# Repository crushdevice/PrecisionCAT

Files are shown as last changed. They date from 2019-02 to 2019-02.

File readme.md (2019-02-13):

PrecisionCAT Software, Hardware Blueprints and Associated Documentation Files
The MIT License (MIT) Copyright (c)

Permission is hereby granted, free of charge, to any person obtaining a copy of this software, hardware blueprints and associated documentation files (the "crush files"), to deal in the crush files without restriction, including without limitation the rights to use, copy, modify, merge, publish, distribute, sublicense, and/or sell copies of the crush files, and to permit persons to whom the crush files is furnished to do so, subject to the following conditions:

The above copyright notice and this permission notice shall be included in all copies or substantial portions of the Software.

THE CRUSH FILES IS PROVIDED "AS IS", WITHOUT WARRANTY OF ANY KIND, EXPRESS OR IMPLIED, INCLUDING BUT NOT LIMITED TO THE WARRANTIES OF MERCHANTABILITY, FITNESS FOR A PARTICULAR PURPOSE AND NONINFRINGEMENT. IN NO EVENT SHALL THE AUTHORS OR COPYRIGHT HOLDERS BE LIABLE FOR ANY CLAIM, DAMAGES OR OTHER LIABILITY, WHETHER IN AN ACTION OF CONTRACT, TORT OR OTHERWISE, ARISING FROM, OUT OF OR IN CONNECTION WITH THE CRUSH FILES OR THE USE OR OTHER DEALINGS IN THE CRUSH FILES.

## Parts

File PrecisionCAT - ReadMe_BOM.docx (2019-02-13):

# PrecisionCAT GitHub Information

Defining the Relationship Between Stress from

Graspers and Bowel Injury in Humans to Establish

Intraoperative Force Boundaries

Khan, Amanda; University of Toronto - Institute of Biomaterials and Biomedical Engineering

MacDonald, Matthew; CIGITI – Hospital for Sick Children, Toronto, ON

Doshi, Sachin; CIGITI – Hospital for Sick Children, Toronto, ON

Streutker, Catherine; University of Toronto Department of Laboratory Medicine and Pathobiology

Rowsell, Corwyn; University of Toronto Department of Laboratory Medicine and Pathobiology

Drake, James; Hospital For Sick Children, Surgery, Neurosurgery, Toronto, ON

Grantcharov, Teodor; University of Toronto Department of Surgery

* Materials and correspondence to: Amanda Farah Khan, amy.khan@mail.utoronto.ca

# Read Me

All SolidWorks and .stl CAD files necessary to manufacture and recreate the PrecisionCAT along with the full Python code necessary to interact with the controller and experimental protocol is located on GitHub and is licensed under the MIT Open Source Initiative:

https://github.com/crushdevice

Load all part files in the PrecisionCAT folder with the main SolidWorks assembly file “PrecisionCATASSEMBLY.SLDASM”.

# Build of Materials

Part | Description | Product Code
SMAC Linear Actuator | 25 mm stroke; 48 volts | https://www.smac-mca.com/lca-series-p-15.html?cPath=1_4 LCA 50-025-72-1F-3
Power Supply | 48 volt | Generic
Omega Load Cell | Miniature universal load cell with ±5 kgF range | https://www.omega.com/pptst/LCM703.html LCM703-5
LAC-1 Controller | Single axis controller; 12-48 volts | https://www.smac-mca.com/lac-single-axis-controller-p-127.html
LAC-1 Communication Kit | Used for interfacing with the controller | Bundled with LAC-1 Controller
Omega Load Cell Strain Gage Amplifier | Bridge excitation of 4 to 15 volts; adjustable gain and offset | https://www.omega.ca/en/communication-and-connectivity/signal-conditioners-and-transmitters/signal-conditioners/dmd-465-series/p/DMD-465 DMD-465
End-Feed Fastener | M6 thread for 30 mm high rail T-slotted framing | https://www.mcmaster.com/5537t527 McMaster-Carr part 5537T527
T-Slotted Framing Single Rail | 1 ft; 30 mm x 30 mm | https://www.mcmaster.com/5537t97 McMaster-Carr part 5537T97
T-Slotted Framing Corner Brackets | For 30 mm | https://www.mcmaster.com/5537t936 McMaster-Carr part 5537T936
316 Stainless Steel Threaded Rod (20 mm) | M6; 1 mm x 20 mm | https://www.mcmaster.com/98863a243 McMaster-Carr part 98863A243
316 Stainless Steel Threaded Rod (40 mm) | M6; 1 mm x 40 mm | https://www.mcmaster.com/98863a260 McMaster-Carr part 98863A260
316 Stainless Steel Thin Hex Nut (M6) | M6; 1 mm | https://www.mcmaster.com/93935a335 McMaster-Carr part 93935A335
316 Stainless Steel Thin Hex Nut (M3) | M3; 0.5 mm | https://www.mcmaster.com/93935a320 McMaster-Carr part 93935A320
Aluminum Plate | 6061 aluminum | Custom milled

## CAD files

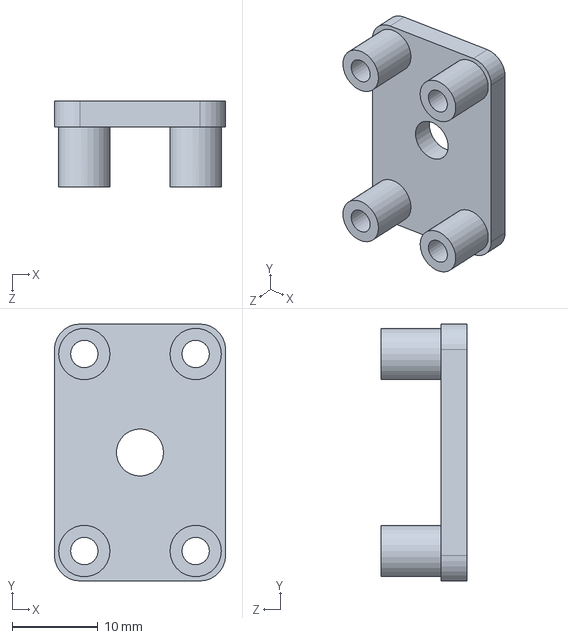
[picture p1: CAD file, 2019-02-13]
Grasper Face 1cm Holder 6mm.SLDPRT
20.0 x 30.0 x 10.0 mm

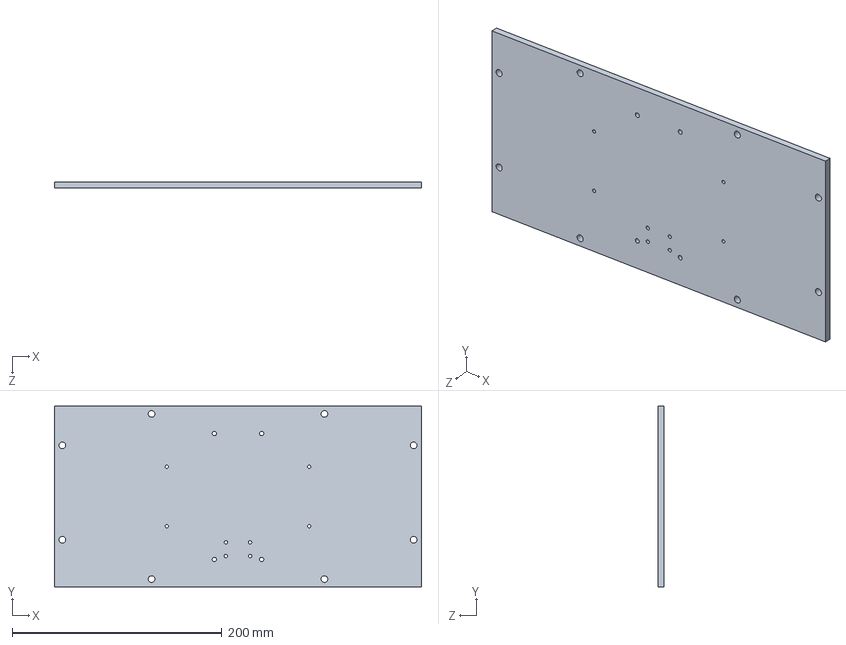
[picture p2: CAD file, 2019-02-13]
Base Plate Al 6mm.SLDPRT
349.8 x 172.5 x 6.00 mm

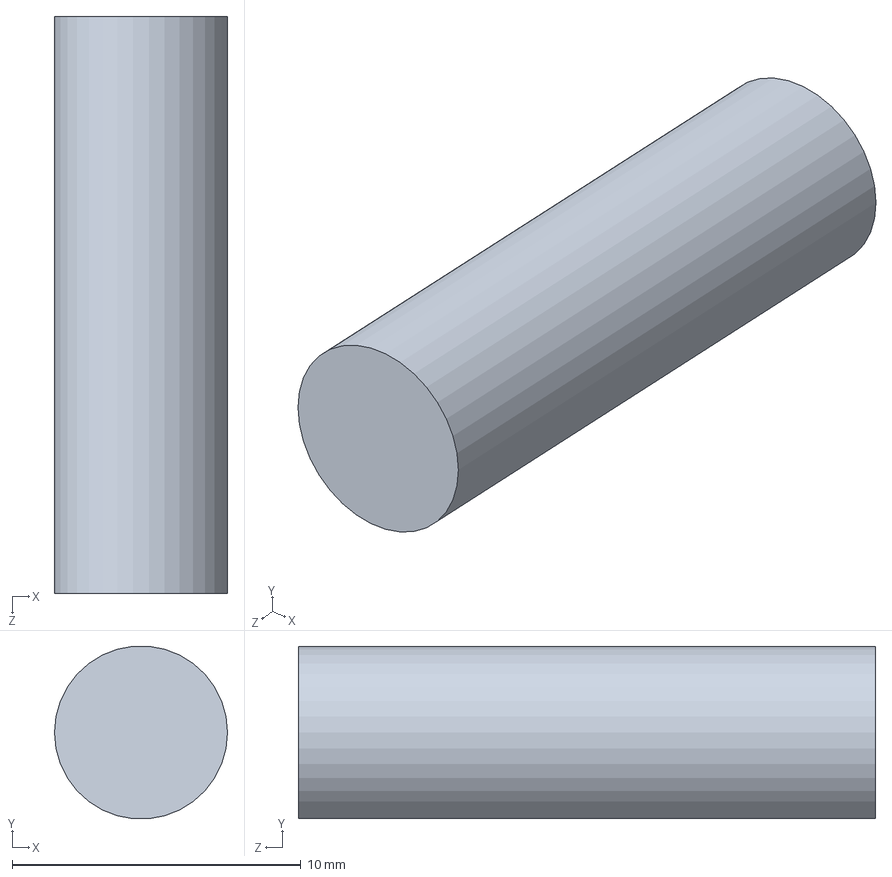
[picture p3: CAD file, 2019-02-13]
Threaded Stud M6.SLDPRT
6.00 x 5.97 x 20.0 mm

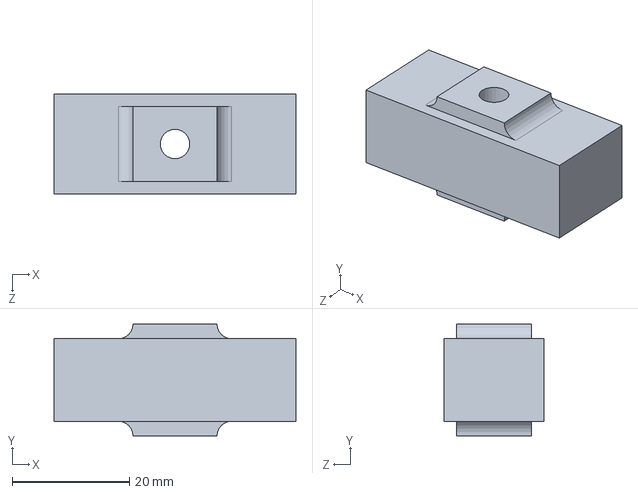
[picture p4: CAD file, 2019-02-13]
Load Cell.SLDPRT
41.2 x 19.1 x 17.1 mm

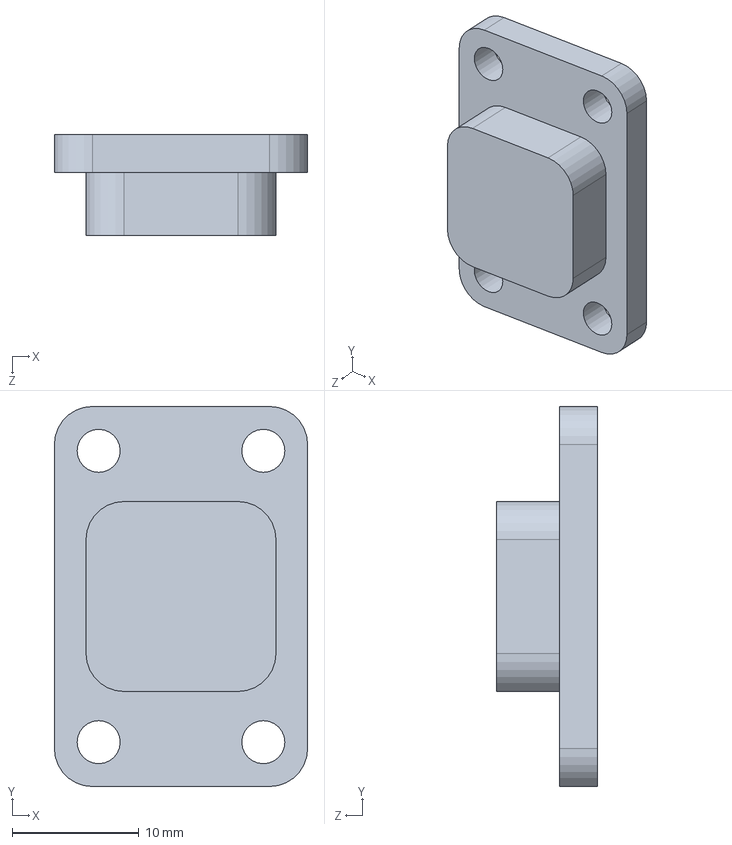
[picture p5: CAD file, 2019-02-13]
Grasper_Plate.SLDPRT
20.0 x 30.0 x 8.00 mm

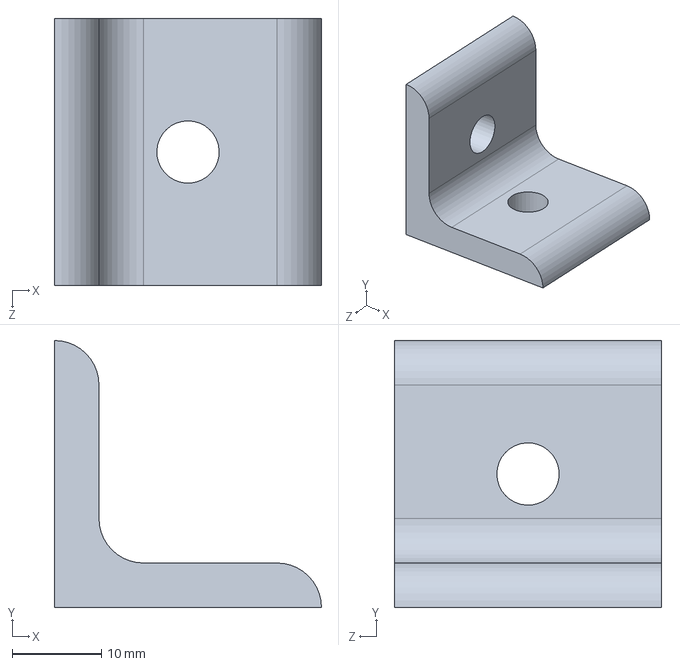
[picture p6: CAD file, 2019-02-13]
3mm_Corner_Mount.SLDPRT
30.0 x 30.0 x 30.0 mm

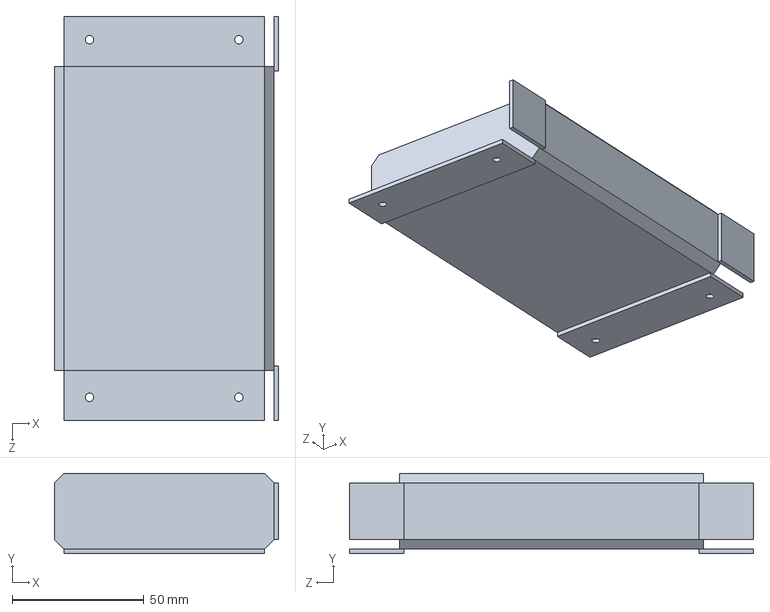
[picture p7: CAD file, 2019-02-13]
LAC-1.SLDPRT
85.2 x 30.4 x 153.2 mm

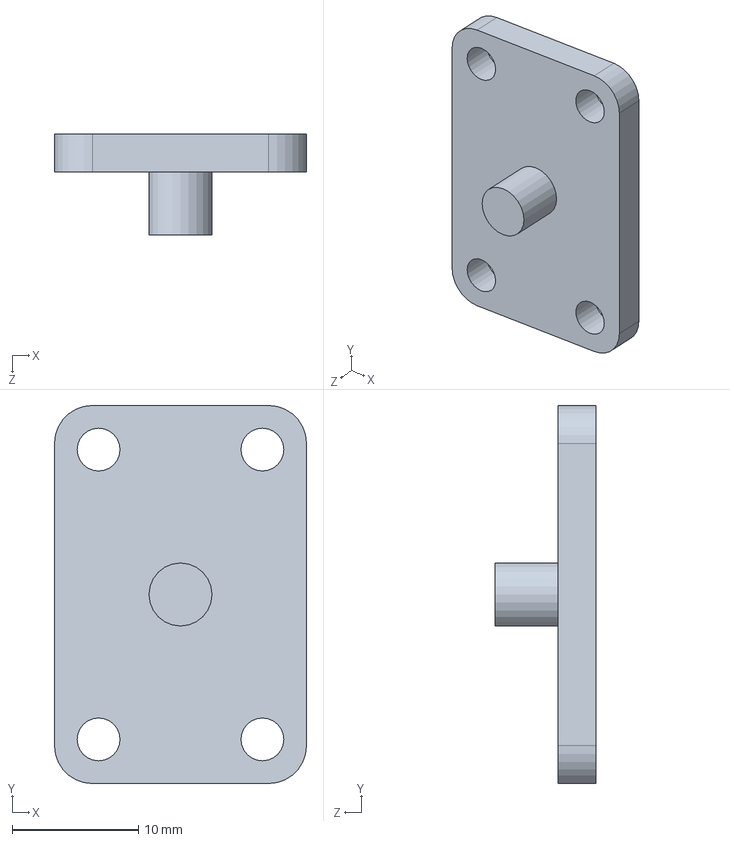
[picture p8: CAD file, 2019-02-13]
Grasper_Pin.SLDPRT
20.0 x 30.0 x 8.00 mm

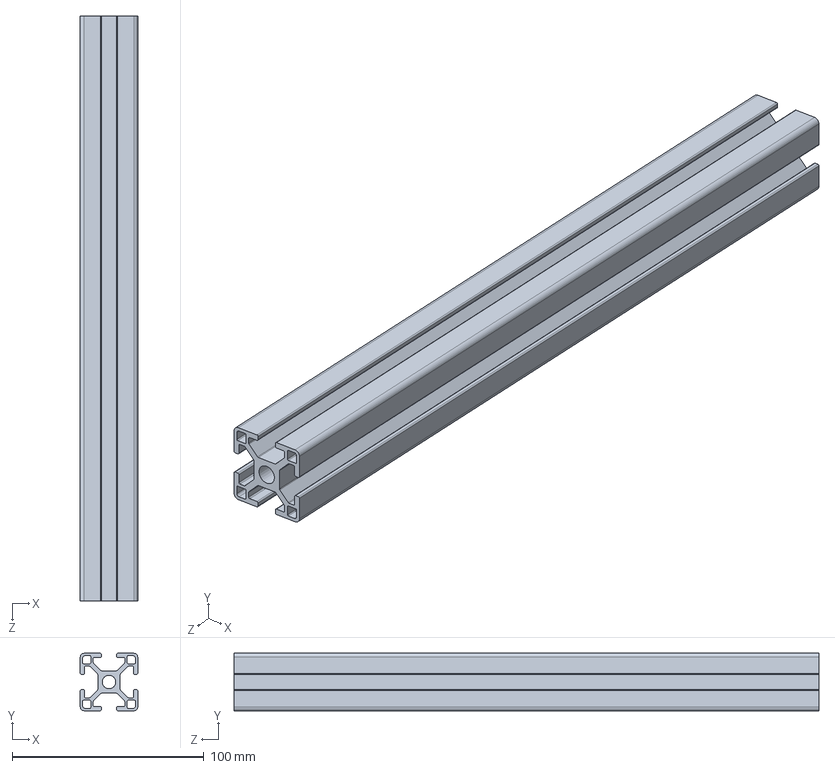
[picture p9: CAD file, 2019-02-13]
3mm_Extrusion_1ft.SLDPRT
30.0 x 30.0 x 304.8 mm

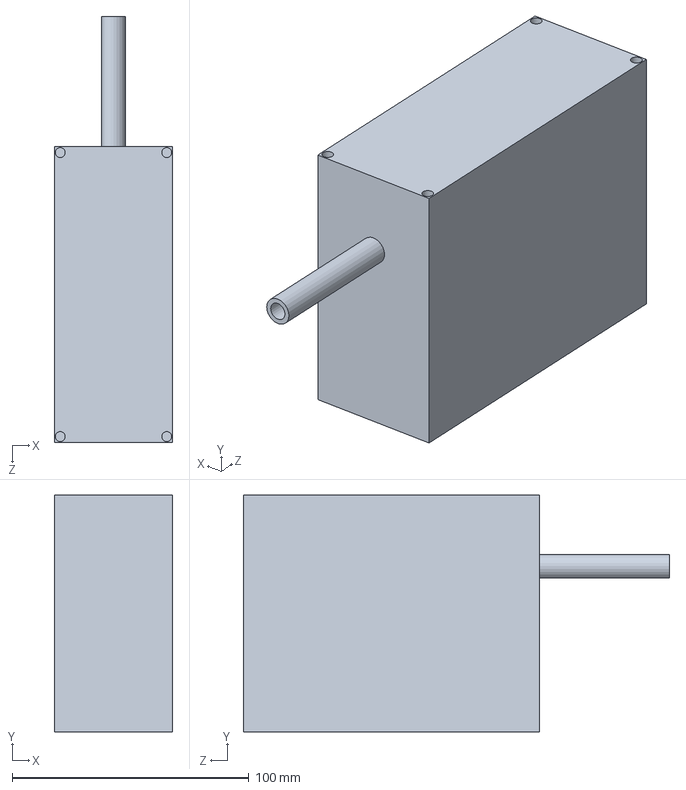
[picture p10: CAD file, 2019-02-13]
SMAC.SLDPRT
50.0 x 100.0 x 180.0 mm

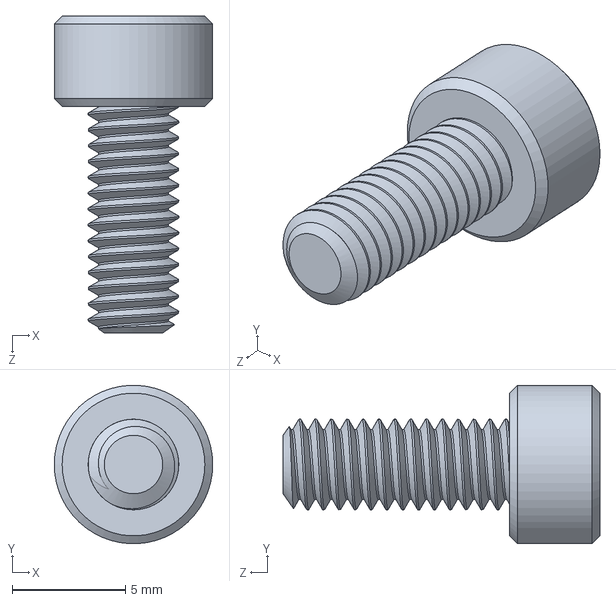
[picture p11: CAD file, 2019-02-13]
92290A144_TYPE 316 SS SOCKET HEAD CAP SCREW.SLDPRT
7.00 x 6.99 x 14.0 mm

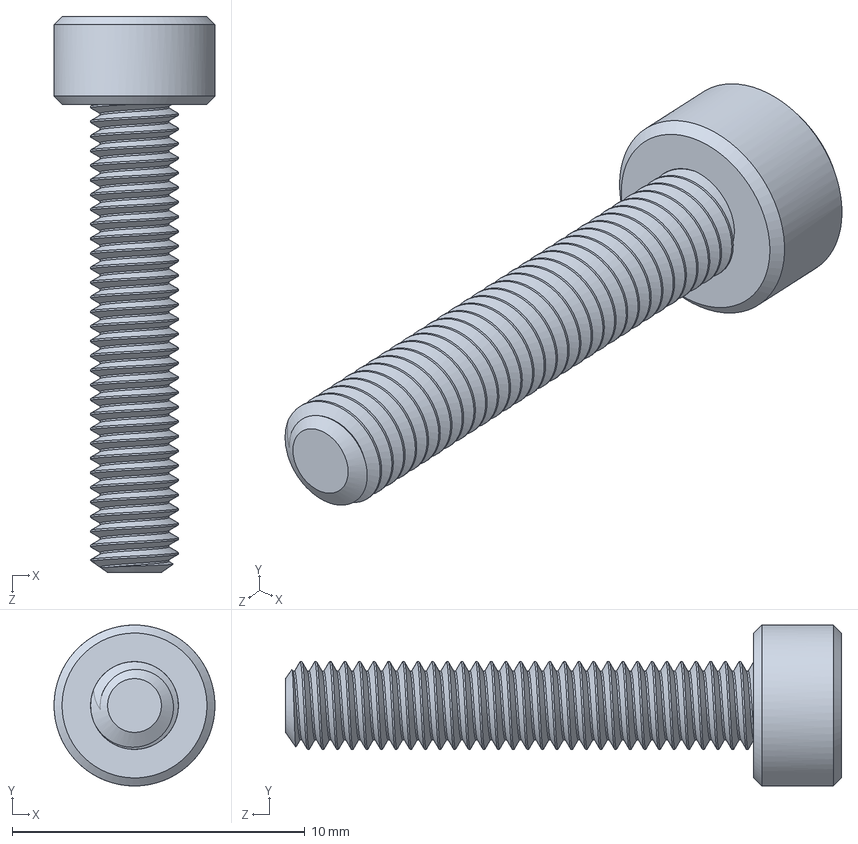
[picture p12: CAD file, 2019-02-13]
92290A120_TYPE 316 SS SOCKET HEAD CAP SCREW.SLDPRT
5.50 x 5.50 x 19.0 mm

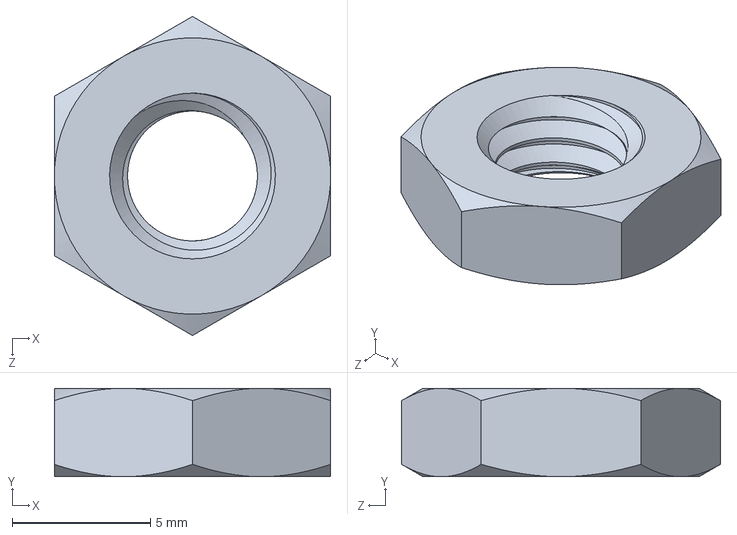
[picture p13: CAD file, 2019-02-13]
93935A335_TYPE 316 SS THIN HEX NUT - DIN 439B.SLDPRT
10.0 x 3.20 x 11.5 mm

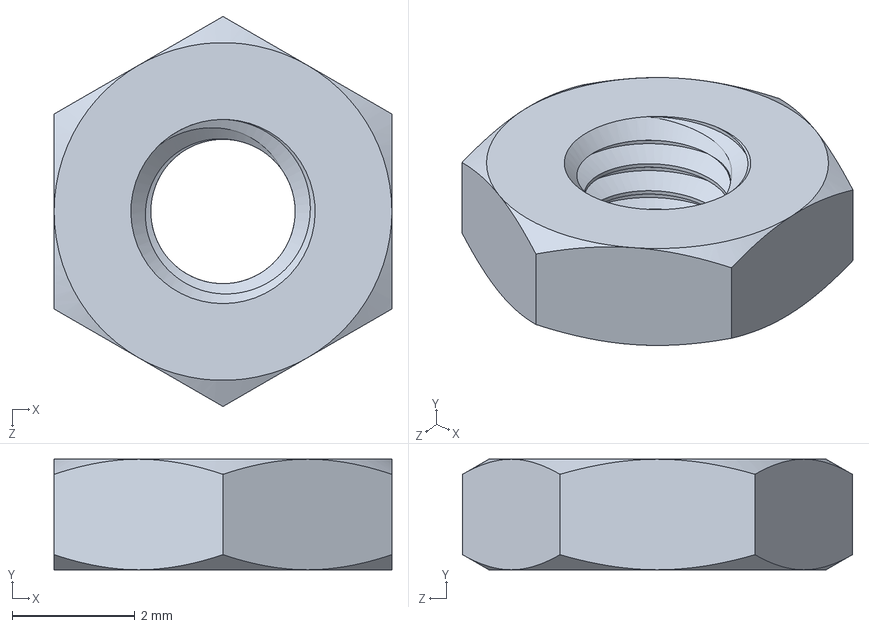
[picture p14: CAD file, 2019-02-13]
93935A320_TYPE 316 SS THIN HEX NUT - DIN 439B.SLDPRT
5.50 x 1.80 x 6.35 mm

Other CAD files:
92290A117_TYPE 316 SS SOCKET HEAD CAP SCREW.SLDPRT

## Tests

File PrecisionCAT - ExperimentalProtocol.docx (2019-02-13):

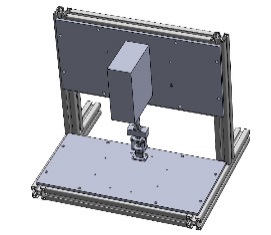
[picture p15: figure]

# PrecisionCAT Experimental Protocol

Defining the Relationship Between Stress from

Graspers and Bowel Injury in Humans to Establish

Intraoperative Force Boundaries

Khan, Amanda; University of Toronto - Institute of Biomaterials and Biomedical Engineering

MacDonald, Matthew; CIGITI – Hospital for Sick Children, Toronto, ON

Doshi, Sachin; CIGITI – Hospital for Sick Children, Toronto, ON

Streutker, Catherine; University of Toronto Department of Laboratory Medicine and Pathobiology

Rowsell, Corwyn; University of Toronto Department of Laboratory Medicine and Pathobiology

Drake, James; Hospital For Sick Children, Surgery, Neurosurgery, Toronto, ON

Grantcharov, Teodor; University of Toronto Department of Surgery

* Materials and correspondence to: Amanda Farah Khan, amy.khan@mail.utoronto.ca

# Python Code

1. Install Anaconda
2. Open Anaconda prompt
3. Type in “ipython”, hit enter
4. Change the loading directory to the folder where your python code is located (via the cd change directory command if necessary); home is autoset to C:\Users\UserID, but set it to the subdirectory where crush.py is located
5. Make sure no tissue is loaded on the tissue loading base and there is nothing obstructing the upper pin plate
6. Type “run crush” then hit enter, the upper crush pin plate will fall to the base then rise back up to home position. This is to calculate distance and zeroing of the plate is important for accurate tissue measurements
7. Choose 0 and hit enter for COM3 serial port (assuming non-Apple PC)
8. Wait for “successfully connected” message to be displayed
9. Type “crush(rig)” then enter
10. Select a protocol by typing in the appropriate number and then hit enter:

0 – stop: crush plate lowers at 5mm/s, then slows to 1mm/s on first contact, continues to slow down if needed to maintain a minimum force resolution, when it hits target force it stops at that position for 10s then goes back to home

1 – hold: same as “stop” but when it hits the target force, it will increase position to maintain that force for a period of 10s, then goes back to home

2 –multi_stop: same as “stop” but repeats for 5 cycles (duty cycle 50%)

3 – multi_hold: same as “hold” but repeats for 5 cycles (duty cycle 50%)

4 – long_stop: same as “stop” but stops in position for 60s instead of 10s

5 – no_stop: same as “stop” but returns to home immediately once target force is reached

11. Input the target load in grams, from 200-1200g = 0 to 11.8 N or 0 to 600 kPa (specifically with our system and pin surface area, 0g, 200g, 400g, 600g, 800g, 1000g and 1200g is approximately equivalent to 2 N, 3.9 N, 5.9 N, 7.8 N, 9.8 N and 11.8 N or 0 kPa, 100 kPa, 200 kPa, 300 kPa, 400 kPa, 500 kPa and 600 kPa)
12. Press enter to run the protocol or x to exit if you made a mistake
13. Messages will display as follows:

Tissue contact made … Target force achieved … Crush complete

14. Once finished type “disconnect(rig)”, crush plate will slowly return to bottom base before depowering

# Experimental Condition 1: Single Load Pressure, “Stop” Protocol

This protocol is “0” or the “stop” protocol. Tissue is compressed for 10 s.

I. Obtain six 1 cm x 1 cm tissue samples. Each sample is loaded onto the grasper plate of the PrecisionCAT serosal side up on a small cellulose-fiber sheet to avoid tissue slippage or curling, one at a time. The grasper pin then needs to be painted with a small precision paintbrush in tissue marking dye (#1003-5 Blue, Davidson Marking System, Minnesota, USA)
II. Once a sample is loaded and is ready to be compressed, enter the force required in grams and run the protocol. Please see above for conversion between grams, Newtons and kPa
III. Load forces to achieve: 0, 200g, 400g, 600g, 800g, 1000g, 1200g
IV. Once the tissue is compressed and the grasp pin plate has returned home, cut the sample in half, with the line of symmetry directly in center of the circle of dye on the tissue. Lay tissue on foam within slide cartridge for orientation.
V. Process tissue samples for hematoxylin and eosin H&E staining.
